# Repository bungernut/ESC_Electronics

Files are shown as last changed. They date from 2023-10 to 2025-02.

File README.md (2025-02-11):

# Board
Order the board at oshpark https://oshpark.com/shared_projects/LPLUU39w

# ESC_Electronics
Digikey: https://www.digikey.com/short/nt3pmbw5

|Reference(s)|Value|Digikey|
|-|-|-|
| BT1, BT2, BT3, BT4, BT5, BT6 | 12V | BH23APC-ND |
| C1, C4 | 10uF | 1276-1096-1-ND |
| C2 | open |  |
| C3, C7 | 1nF | 399-CGP1C102KNYDAAWL25-ND |
| C5 | 1pF | 445-180733-1-ND |
| C6 | 4700pF | 399-CGP1C472MNWDAAWL25-ND |
| C8 | open |  |
| C9, C10, C15, C16 | 0.1uF | 1276-1003-1-ND |
| C11, C12 | 330uF | 1189-1766-ND |
| C13, C14 | 0.33uF | 1276-2926-1-ND |
| D1, D2 | RB751V-40 | MBR0540TPMSCT-ND |
| F1, F2 | Polyfuse_Small | 507-1794-1-ND |
| FB1, FB2 | FerriteBead_Small | 732-6715-1-ND |
| H1, H2, H3, H4 | MountingHole |  |
| H5 | DiodeFeedThru |  |
| H6, H7 | MountingHole |  |
| J1 | Batt probe | N/A |
| J2 | CA probe | N/A |
| J3 | Test Input BNC | ARF2005-ND |
| J4 | -1000VDC SHV | 4912-SHV-BR-ND |
| J5 | RV Prob |  |
| J6 | Output BNC | ARF2005-ND |
| J7 | DC Power | WM4825-ND |
| J8 | -8V |  |
| J9 | +8V |  |
| R1 | open |  |
| R2, R3, R5 | 10M | HVA12FA10M0CT-ND |
| R4 | 100M | HVA12FA100MCT-ND |
| R6 | 47 | RPC0805JT47R0 |
| R7 | open |  |
| R8 | 0 | RMCF0805ZT0R00 |
| R9 | 750 | RMCF0805FT750RCT-ND |
| R10 | 20k | RMCF0805FT20K0CT-ND |
| RV1 | 10k | 3266W-103LF-ND |
| U1 | CR110 | ED11161-ND |
| U2 | SiPhotodiode |  |
| U3 | TL051CP | 296-7192-5-ND |
| U4 | UA78M08 | 296-12612-1-ND |
| U5 | UA79M08 | 296-19678-1-ND |

Other items for assembly:
| Part | Ref | Link |
|-|-|-|
| Cremat CR110 | U1 | https://www.cremat.com/home/charge-sensitive-preamplifiers/ |
| SiDiode | U2 | https://www.hamamatsu.com/us/en/product/optical-sensors/photodiodes/si-photodiodes/S3204-09.html |
| 8 PDIP Socket | U3 |  https://www.digikey.com/en/products/detail/te-connectivity-amp-connectors/1-2199298-2/5022039 |
| Red HV Hookup Wire | | https://www.digikey.com/en/products/detail/cnc-tech/3239-24-1-0500-004-1-TS/5968804 |
| BLK HV Hookup Wire | | https://www.digikey.com/en/products/detail/cnc-tech/3239-24-1-0500-001-1-TS/5968800 |
| Electronic Box | | https://www.digikey.com/en/products/detail/bud-industries/CN-5709/1219181 |
| SHV Bulkhead | | https://www.digikey.com/en/products/detail/te-connectivity-amp-connectors/51494-2/298100 |
| Power Cable Assembly | | https://www.digikey.com/en/products/detail/te-connectivity-amp-connectors/2273001-1/5167970 |
| Power Cable Feedthrough | | https://www.digikey.com/en/products/detail/te-connectivity-amp-connectors/T4030014031-000/7927423 |
| Power Supply | | https://www.digikey.com/en/products/detail/xp-power/ECL15UD01-S/4487543 |
| Power Resistors (2x) | | https://www.digikey.com/en/products/detail/ohmite/HS50-100R-J/5307799 |
| AC power feedthrough | | https://www.digikey.com/en/products/detail/davies-molding-llc/GC1000-A/7795436 |

Photo of a completed board:

e-board

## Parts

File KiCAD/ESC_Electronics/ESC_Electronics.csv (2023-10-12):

# | Reference | Qty | Value | Footprint | DNP
1 | BT1, BT2, BT3, BT4, BT5, BT6 | 6 | 12V | ESC_Electronics_Library:6S-Battery-Holder
2 | C1, C4 | 2 | 10uF | Capacitor_SMD:C_0805_2012Metric_Pad1.18x1.45mm_HandSolder
3 | C2 | 1 | open | Capacitor_THT:C_Disc_D7.5mm_W5.0mm_P5.00mm
4 | C3, C7 | 2 | 1nF | Capacitor_THT:C_Disc_D10.5mm_W5.0mm_P10.00mm
5 | C5 | 1 | 1pF | Capacitor_THT:C_Disc_D7.5mm_W5.0mm_P5.00mm
6 | C6 | 1 | 4700pF | Capacitor_THT:C_Disc_D12.5mm_W5.0mm_P10.00mm
7 | C8 | 1 | open | Capacitor_SMD:C_0805_2012Metric_Pad1.18x1.45mm_HandSolder
8 | C9, C10, C15, C16 | 4 | 0.1uF | Capacitor_SMD:C_0805_2012Metric_Pad1.18x1.45mm_HandSolder
9 | C11, C12 | 2 | 330uF | Capacitor_THT:CP_Radial_D10.0mm_P5.00mm
10 | C13, C14 | 2 | 0.33uF | Capacitor_SMD:C_0805_2012Metric_Pad1.18x1.45mm_HandSolder
11 | D1, D2 | 2 | RB751V-40 | Diode_SMD:D_SOD-123
12 | FB1, FB2 | 2 | FerriteBead_Small | Inductor_SMD:L_1206_3216Metric_Pad1.22x1.90mm_HandSolder
13 | H1, H2, H3, H4 | 4 | MountingHole | MountingHole:MountingHole_3.2mm_M3
14 | H5 | 1 | DiodeFeedThru | ESC_Electronics_Library:DiodeFeedThru
15 | H6, H7 | 2 | MountingHole | ESC_Electronics_Library:4headclear
16 | J1 | 1 | Batt probe | Connector_PinHeader_2.54mm:PinHeader_1x02_P2.54mm_Vertical
17 | J2 | 1 | CA probe | Connector_PinHeader_2.54mm:PinHeader_1x02_P2.54mm_Vertical
18 | J3 | 1 | Test Input BNC | Connector_Coaxial:BNC_Amphenol_B6252HB-NPP3G-50_Horizontal
19 | J4 | 1 | -1000VDC SHV | ESC_Electronics_Library:MHV Wire Conn
20 | J5 | 1 | RV Prob | Connector_PinHeader_2.54mm:PinHeader_1x02_P2.54mm_Vertical
21 | J6 | 1 | Output BNC | Connector_Coaxial:BNC_Amphenol_B6252HB-NPP3G-50_Horizontal
22 | J7 | 1 | DC Power | Connector_Molex:Molex_KK-254_AE-6410-03A_1x03_P2.54mm_Vertical
23 | J8 | 1 | -8V | Connector_PinHeader_2.54mm:PinHeader_1x02_P2.54mm_Vertical
24 | J9 | 1 | +8V | Connector_PinHeader_2.54mm:PinHeader_1x02_P2.54mm_Vertical
25 | R1 | 1 | open | Resistor_THT:R_Axial_DIN0207_L6.3mm_D2.5mm_P5.08mm_Vertical
26 | R2, R3, R5 | 3 | 10M | Resistor_THT:R_Axial_DIN0207_L6.3mm_D2.5mm_P15.24mm_Horizontal
27 | R4 | 1 | 100M | Resistor_THT:R_Axial_DIN0207_L6.3mm_D2.5mm_P15.24mm_Horizontal
28 | R6 | 1 | 47 | Resistor_SMD:R_0805_2012Metric_Pad1.20x1.40mm_HandSolder
29 | R7 | 1 | open | Resistor_THT:R_Axial_DIN0207_L6.3mm_D2.5mm_P15.24mm_Horizontal
30 | R8 | 1 | 0 | Resistor_SMD:R_1206_3216Metric_Pad1.30x1.75mm_HandSolder
31 | R9 | 1 | 750 | Resistor_SMD:R_0805_2012Metric_Pad1.20x1.40mm_HandSolder
32 | R10 | 1 | 20k | Resistor_SMD:R_0805_2012Metric_Pad1.20x1.40mm_HandSolder
33 | RV1 | 1 | 10k | Potentiometer_THT:Potentiometer_Bourns_3266W_Vertical
34 | U1 | 1 | CR110 | Connector_PinHeader_2.54mm:PinHeader_1x08_P2.54mm_Vertical
35 | U2 | 1 | SiPhotodiode | Connector_Wire:SolderWire-0.5sqmm_1x02_P4.6mm_D0.9mm_OD2.1mm
36 | U3 | 1 | TL051CP | Package_DIP:DIP-8_W7.62mm_Socket
37 | U4 | 1 | UA78M08 | Package_TO_SOT_SMD:SOT-223-3_TabPin2
38 | U5 | 1 | UA79M08 | ESC_Electronics_Library:TO-252-3_Tab1

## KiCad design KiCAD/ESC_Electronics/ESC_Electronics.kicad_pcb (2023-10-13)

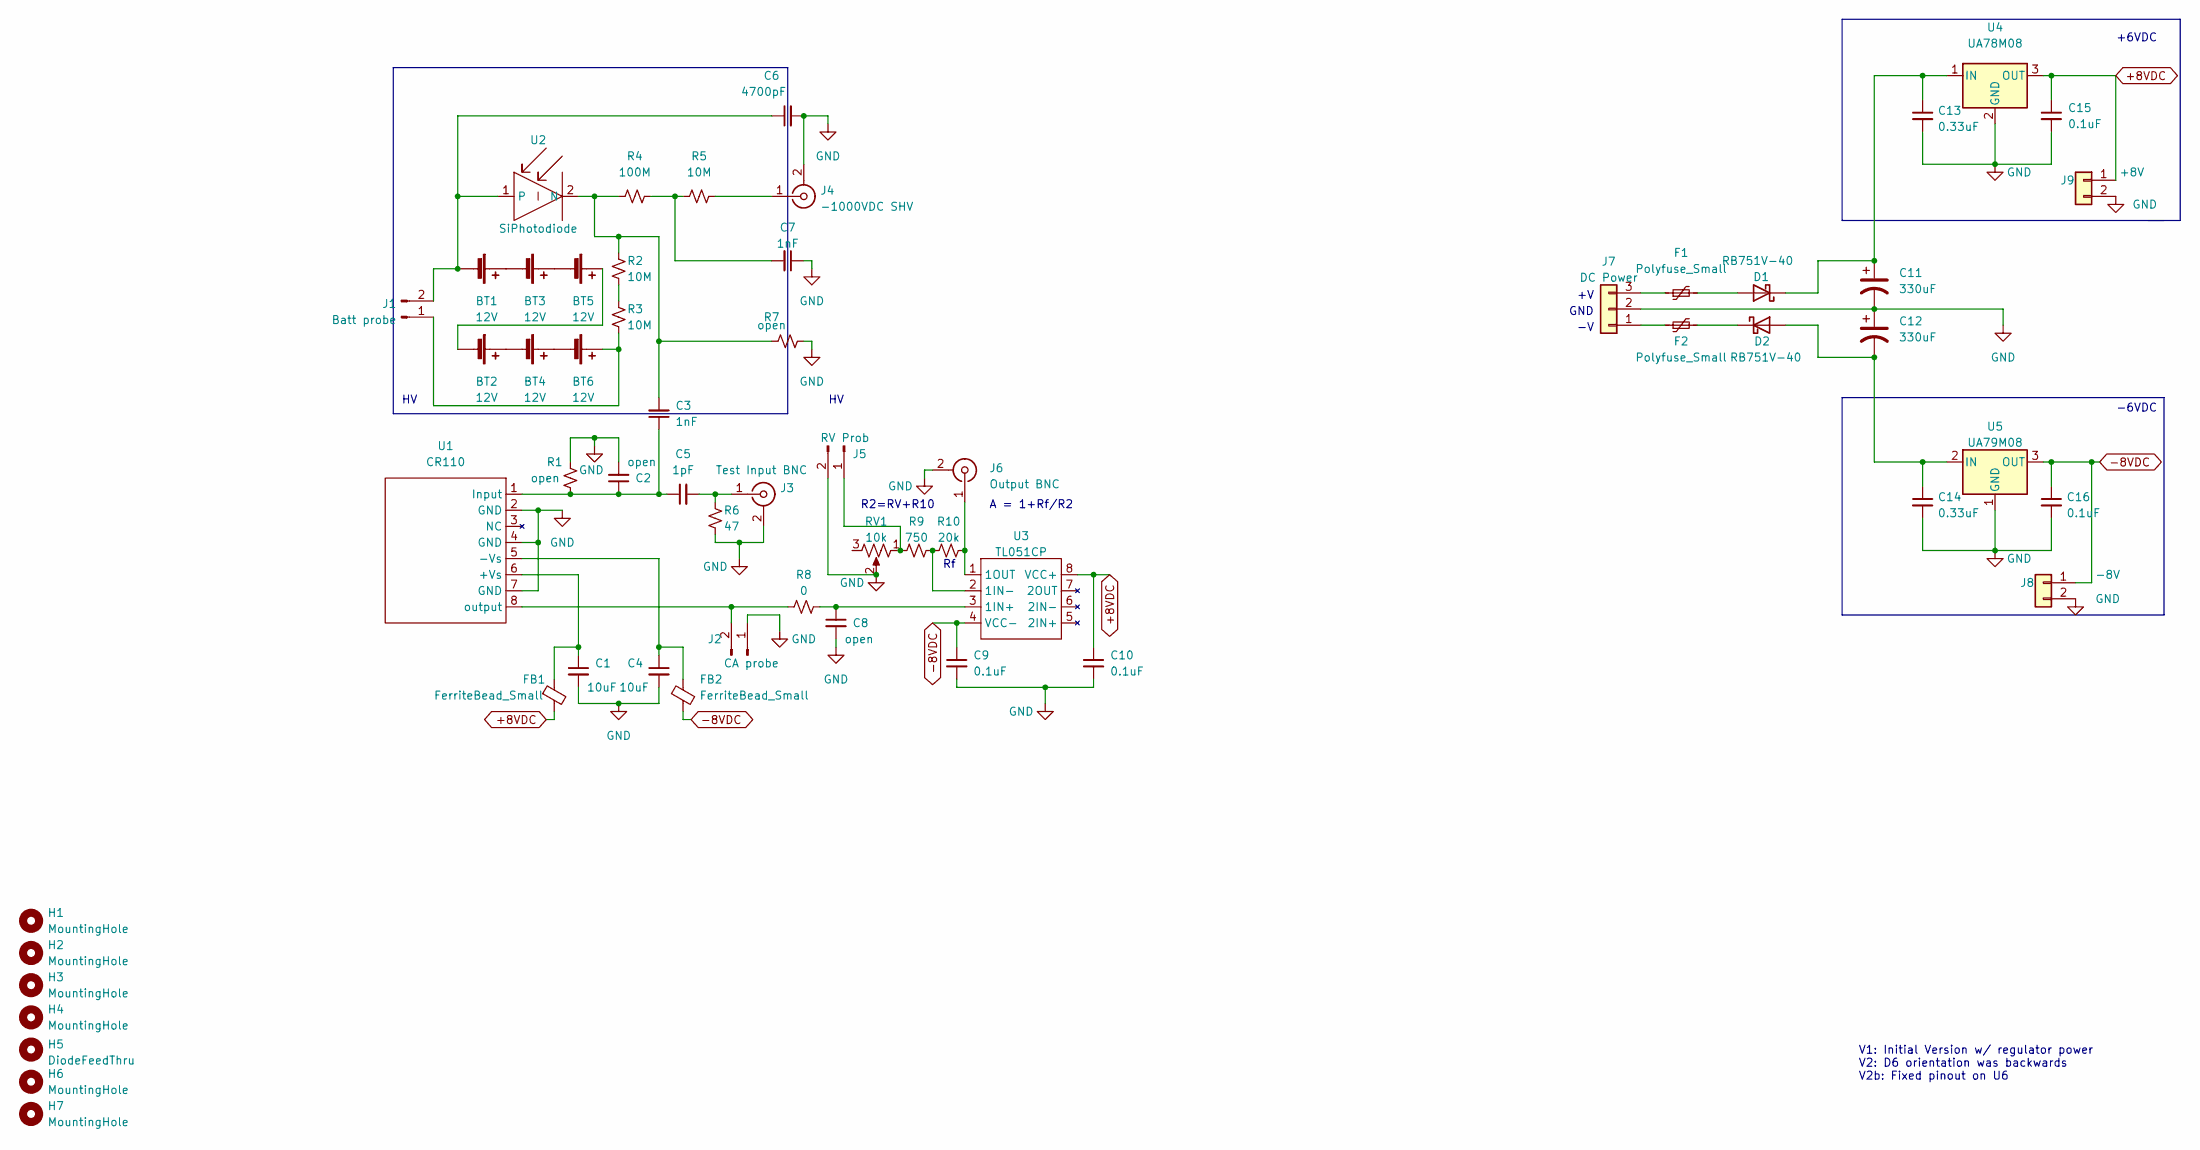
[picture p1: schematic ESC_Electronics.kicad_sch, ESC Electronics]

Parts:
BT1, BT2, BT3, BT4, BT5, BT6: 12V; 6S-Battery-Holder; Digikey BH23APC-ND
C1, C4: 10uF; C_0805_2012Metric_Pad1.18x1.45mm_HandSolder; Digikey 1276-1096-1-ND
C2: open; C_Disc_D7.5mm_W5.0mm_P5.00mm
C3, C7: 1nF; C_Disc_D10.5mm_W5.0mm_P10.00mm; Digikey 399-CGP1C102KNYDAAWL25-ND
C5: 1pF; C_Disc_D7.5mm_W5.0mm_P5.00mm; Digikey 445-180733-1-ND
C6: 4700pF; C_Disc_D12.5mm_W5.0mm_P10.00mm; Digikey 399-CGP1C472MNWDAAWL25-ND
C8: open; C_0805_2012Metric_Pad1.18x1.45mm_HandSolder
C9, C10, C15, C16: 0.1uF; C_0805_2012Metric_Pad1.18x1.45mm_HandSolder; Digikey 1276-1003-1-ND
C11, C12: 330uF; CP_Radial_D10.0mm_P5.00mm; Digikey 1189-1766-ND
C13, C14: 0.33uF; C_0805_2012Metric_Pad1.18x1.45mm_HandSolder; Digikey 1276-2926-1-ND
D1, D2: RB751V-40; D_SOD-123; Digikey MBR0540TPMSCT-ND
F1, F2: Polyfuse_Small; R_1210_3225Metric_Pad1.30x2.65mm_HandSolder; Digikey 507-1794-1-ND
FB1, FB2: FerriteBead_Small; L_1206_3216Metric_Pad1.22x1.90mm_HandSolder; Digikey 732-6715-1-ND
H1, H2, H3, H4: MountingHole; MountingHole_3.2mm_M3
H5: DiodeFeedThru
H6, H7: MountingHole; 4headclear
J1: Batt probe; PinHeader_1x02_P2.54mm_Vertical; Digikey N/A
J2: CA probe; PinHeader_1x02_P2.54mm_Vertical; Digikey N/A
J3: Test Input BNC; BNC_Amphenol_B6252HB-NPP3G-50_Horizontal; Digikey ARF2005-ND
J4: -1000VDC SHV; MHV Wire Conn; Digikey 4912-SHV-BR-ND
J5: RV Prob; PinHeader_1x02_P2.54mm_Vertical
J6: Output BNC; BNC_Amphenol_B6252HB-NPP3G-50_Horizontal; Digikey ARF2005-ND
J7: DC Power; Molex_KK-254_AE-6410-03A_1x03_P2.54mm_Vertical; Digikey WM4825-ND
J8: -8V; PinHeader_1x02_P2.54mm_Vertical
J9: +8V; PinHeader_1x02_P2.54mm_Vertical
R1: open; R_Axial_DIN0207_L6.3mm_D2.5mm_P5.08mm_Vertical
R2, R3, R5: 10M; R_Axial_DIN0207_L6.3mm_D2.5mm_P15.24mm_Horizontal; Digikey HVA12FA10M0CT-ND
R4: 100M; R_Axial_DIN0207_L6.3mm_D2.5mm_P15.24mm_Horizontal; Digikey HVA12FA100MCT-ND
R6: 47; R_0805_2012Metric_Pad1.20x1.40mm_HandSolder; Digikey RPC0805JT47R0
R7: open; R_Axial_DIN0207_L6.3mm_D2.5mm_P15.24mm_Horizontal
R8: 0; R_1206_3216Metric_Pad1.30x1.75mm_HandSolder; Digikey RMCF0805ZT0R00
R9: 750; R_0805_2012Metric_Pad1.20x1.40mm_HandSolder; Digikey RMCF0805FT750RCT-ND
R10: 20k; R_0805_2012Metric_Pad1.20x1.40mm_HandSolder; Digikey RMCF0805FT20K0CT-ND
RV1: 10k; Potentiometer_Bourns_3266W_Vertical; Digikey 3266W-103LF-ND
U1: CR110; PinHeader_1x08_P2.54mm_Vertical; Digikey ED11161-ND
U2: SiPhotodiode; SolderWire-0.5sqmm_1x02_P4.6mm_D0.9mm_OD2.1mm
U3: TL051CP; DIP-8_W7.62mm_Socket; Digikey 296-7192-5-ND
U4: UA78M08; SOT-223-3_TabPin2; Digikey 296-12612-1-ND
U5: UA79M08; TO-252-3_Tab1; Digikey 296-19678-1-ND

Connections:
+8VDC: C10.1, C15.1, FB1.2, J9.1, U3.8 (VCC+), U4.3 (OUT)
-8VDC: C9.1, C16.1, FB2.2, J8.1, U3.4 (VCC-), U5.3 (OUT)
GND: C1.2, C2.2, C4.2, C6.2, C7.1, C8.2, C9.2, C10.2, C11.2, C12.1, C13.2, C14.2, C15.2, C16.2, J2.1, J3.2 (Ext), J4.2 (Ext), J5.2, J6.2 (Ext), J7.2, J8.2, J9.2, R1.2, R6.2, R7.2, RV1.2, U1.2 (GND), U1.4 (GND), U1.7 (GND), U4.2 (GND), U5.1 (GND)
unnamed: BT1.1 (+), BT3.2 (-)
unnamed: BT1.2 (-), C6.1, J1.2, U2.1
unnamed: BT2.1 (+), BT4.2 (-)
unnamed: BT2.2 (-), BT5.1 (+)
unnamed: BT3.1 (+), BT5.2 (-)
unnamed: BT4.1 (+), BT6.2 (-)
unnamed: BT6.1 (+), J1.1, R3.1
unnamed: C7.2, R4.2, R5.1
unnamed: D1.2 (A), F1.2
unnamed: C11.1, C13.1, D1.1 (K), U4.1 (IN)
unnamed: C12.2, C14.1, D2.2 (A), U5.2 (IN)
unnamed: D2.1 (K), F2.2
unnamed: J2.2, R8.1, U1.8 (output)
unnamed: C5.2, J3.1 (In), R6.1
unnamed: J4.1 (In), R5.2
unnamed: J5.1, R9.1, RV1.1
unnamed: J6.1 (In), R10.2, U3.1 (1OUT)
unnamed: F2.1, J7.1
unnamed: F1.1, J7.3
unnamed: R2.1, R3.2
unnamed: C1.1, FB1.1, U1.6 (+Vs)
unnamed: C4.1, FB2.1, U1.5 (-Vs)
unnamed: C2.1, C3.1, C5.1, R1.1, U1.1 (Input)
unnamed: C3.2, R2.2, R4.1, R7.1, U2.2 (N)
unnamed: C8.1, R8.2, U3.3 (1IN+)
unnamed: R9.2, R10.1, U3.2 (1IN-)

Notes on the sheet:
+6VDC
-6VDC
GND
V1: Initial Version w/ regulator power V2: D6 orientation was backwards V2b: Fixed pinout on U6
R2=RV+R10
A = 1+Rf/R2

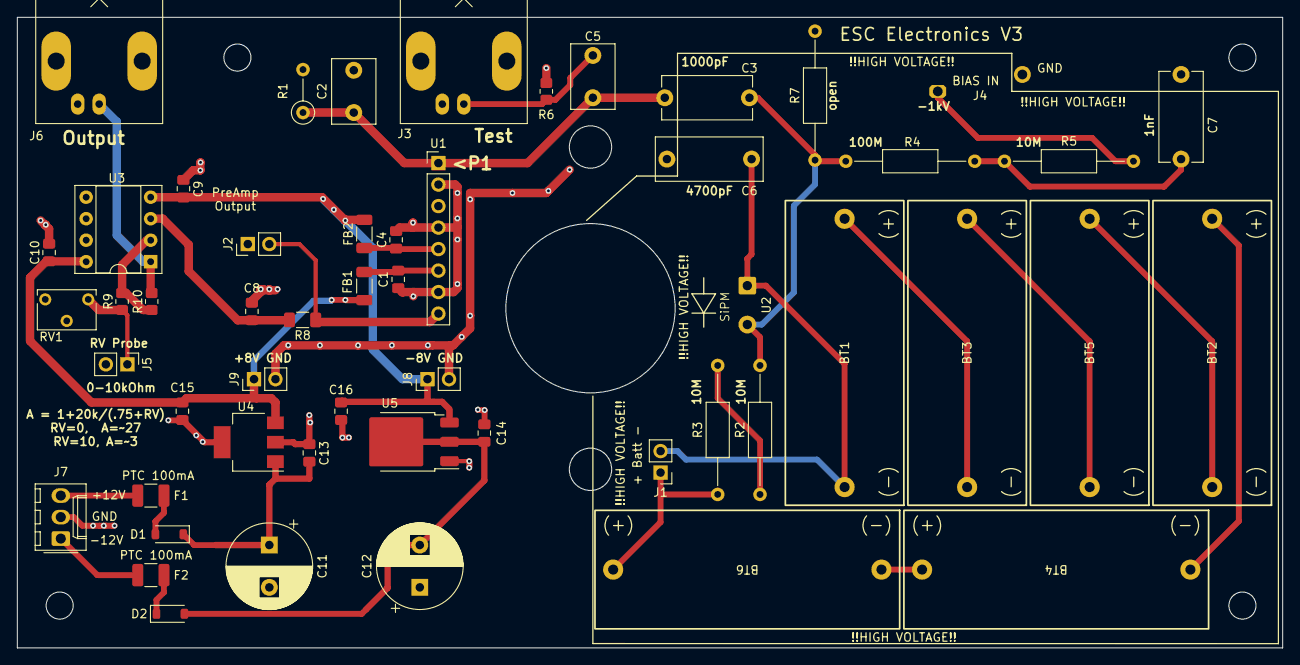
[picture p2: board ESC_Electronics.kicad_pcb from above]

Board: 2 copper layers, 149.5 x 74.5 mm, 60 parts (0 on the bottom side), 29 nets.

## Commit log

2022-08-17 laying out V1
    [ESC_Electronics.kicad_pcb, ESC_Electronics.kicad_sch]
2022-08-17 layed out board
    [ESC_Electronics.kicad_pcb, ESC_Electronics.kicad_sch]
2022-08-19 uploaded this version to OSHpark as V1
    [ESC_Electronics.csv, ESC_Electronics.kicad_pcb, ESC_Electronics.kicad_sch]
2022-08-19 the real ESC V1
    [ESC_Electronics.kicad_pcb, ESC_Electronics.kicad_sch]
2022-10-11 Refining for V2 while debugging
    [ESC_Electronics.kicad_pcb, ESC_Electronics.kicad_sch]
2022-10-11 Refining for V2 while debugging R2
    [ESC_Electronics.kicad_pcb, ESC_Electronics.kicad_sch]
2022-10-11 Refining for V2 while debugging R3
    [ESC_Electronics.kicad_pcb, ESC_Electronics.kicad_sch]
2022-10-17 Refining for V2 while debugging R4
    [ESC_Electronics.kicad_pcb, ESC_Electronics.kicad_sch]
2022-11-09 published as V2 on OSHPark
    [ESC_Electronics.kicad_pcb, ESC_Electronics.kicad_sch]
2023-06-30 fixed U6 pad and updated several footprints to latest KiCAD versions
    [ESC_Electronics.kicad_pcb, ESC_Electronics.kicad_sch]
2023-06-30 Updated PDB label to V2b for #4 fix
    [ESC_Electronics.kicad_pcb]
2023-07-06 Updating Digikey Partnumbers
    [ESC_Electronics.kicad_sch]
2023-07-06 Cleaning up SCH w/ notes
    [ESC_Electronics.kicad_pcb, ESC_Electronics.kicad_sch]
2023-08-08 Another mistake on the Neg8V resistor
    [ESC_Electronics.kicad_pcb]
2023-09-27 Modification for external PS
    [ESC_Electronics.kicad_pcb, ESC_Electronics.kicad_sch]
2023-10-12 Updating docs
    [ESC_Electronics.csv, ESC_Electronics.kicad_sch]
2023-10-13 added PTC to power input
    [ESC_Electronics.kicad_pcb, ESC_Electronics.kicad_sch]
2023-10-13 Updating Readme
    [ESC_Electronics.kicad_sch]
2025-02-11 Update README.md
    added photo of a completed board
